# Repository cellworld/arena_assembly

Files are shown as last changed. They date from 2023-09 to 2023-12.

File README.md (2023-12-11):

# Cellworld Arena Assembly
<!-- ![Alt Text](https://github.com/cellworld/arena_assembly/blob/main/Images/cellworld_components-01.png) -->
<p align="center">
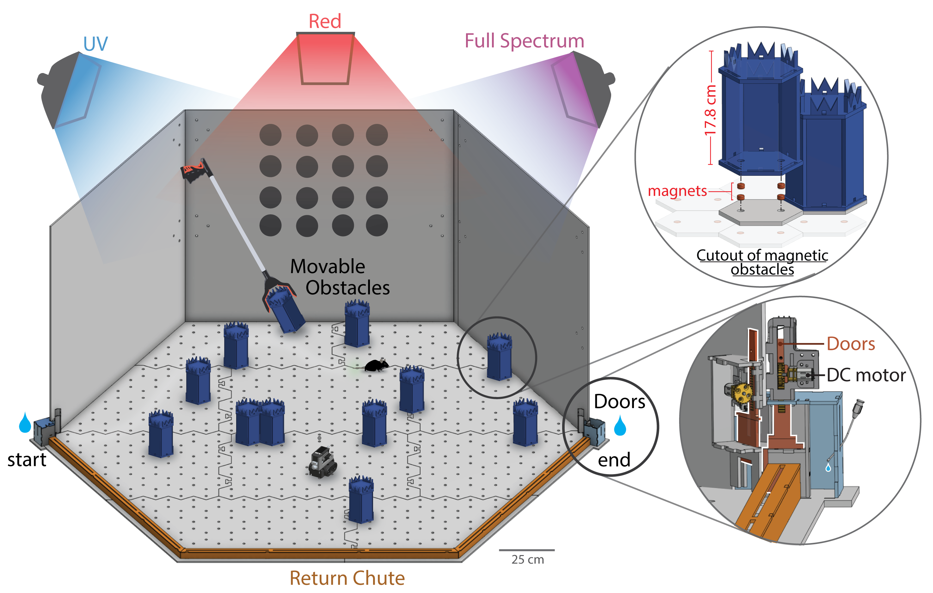
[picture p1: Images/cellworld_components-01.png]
arena_overview
  
</p>

All parts of the arena can be found in the STEP files of this github repository. <b>However, to see how the parts assemble on 
a web browser, you can use this [Onshape link](https://cad.onshape.com/documents/c8897f9f1e8291dd2da7ef89/w/1c35d23167742132946594eb/e/1fb43747d3ac53d540c92c7f?renderMode=0&uiState=64f8d54faca3cb0d59202402z)</b>.

Files in this repository are based on the Onshape CAD file system where we designed components in part studios and then imported them into assemblies 
to determine their interaction with other parts. Assemblies are good for visualizing how components are placed together for construction. 
When using the Onshape link, the assemblies will be the first files you will see, and
you can both manipulate objects within the assemblies and export them (as well are parts from the part studios) to whatever file format you need. 
For creating drawings for laser cutting or STL files for 3D printing however, we recommend using our part studios files.

Components of the arena can be devised into four components: the arena itself, the automated door system, the obstacles, and the water feeder system. 
Construction within each of these categories will be described below, but all parts are derived from either laser-cut acrylic or 3D printing.
Parts that need to be 3D printed will have the string "3D_PRINT" inserted at the beginning of the part's name.
Step files will have multiple parts included in them.

## The Arena
The arena consists of the arena floor, arena walls, general chamber structures, and the return chute. 
Please use the *Final Arena.step*  to grab all the parts. The one arena wall
opposite of the return chute center is replaced by the *Human Door.step* to allow for easy entry of the researcher. 

With exception to the wall binders (which are 3D printed), all parts are cut from white acrylic. All chamber and return chute components (the walls and ceilings) 
use 3.175 mm thick white acrylic, but all other parts use 6.35 mm thick white acrylic.

Please refer to the *Cellworld Arena.step* file in the *Assemblies* directory to see how all parts should fit.

Specialized Parts:
* 11.11 mm diameter neodymium magnets (D74-N52, K&J Magnetics, Pipersville, PA, USA)
* Red light bulbs (LED Red light therapy bulb, Wolezek LED, China)
* Full spectrum growth lights (9-Watt LED Grow Light Bulb, General Electric, Boston, MA, USA)
* UV light bulbs (UV LED Black lights Bulb, SHGPODA, Shenzhen, Guangdong, China)
* White noise generator (LectroFan Classic, Campbell, CA, USA)

Construction:
1. Assemble floor panels together and insert magnets into floor slots with superglue.
2. Assemble *Human Door.step* using 80/20 25.4 mm aluminum as a frame. Hinges can be added to the aluminum frame for the door.
2. Slot walls and human door into the floor.
2. Attach 3D-printed wall binders using bolts to connect walls together.
3. Add layer of hand-cut clear vinyl (to the shape of the arena) over arena floor.
4. Seal connections between arena walls and 3.175 mm thick clear vinyl floor with silicone sealant.
5. Slot chamber walls and return chute walls into floor.
6. Seal connections between chamber/return chute walls and the floor with silicone sealant.
7. Attach chamber and return chute ceilings. For return chute ceilings we added sticky magnets to the outside of the
arena walls and to the return chute ceiling for easy attachment.
8. Bond introduction chamber walls (minus the "Introduction Sliding Wall") together with the introduction chamber floor using liquid solvent for acrylic bonding (#4 Acrlyic Adhesive, Weld-On, Compton, CA, USA).
9. Insert magnets using superglue into "Introduction Chamber Wall" and the "Introduction Door Blocker".
10. Place light bulbs in the softbox and place in the arena.
11. Mount white noise generator near arena and above the arena walls.

## The Door System
This is the most complex component of the arena to assemble. Three main STEP files will be used to create the structure of the doors:
*END Door Housing.step*, *START outer door support.step*, and *START inner door support.step*. 
To note, all these components are associated with either the START or END chamber (indicated by their name), 
however, all parts can work with both chambers as they are simply mirrored before construction. 
In many cases, this might mean simply flipping parts during assembly.

Files labeled as the "door support" are the components that hold the 
DC motors, limit switches, and silicone/laser cut doors, keeping them in place so that the gear on the motors precisely interacts with the rail inserted into the doors. 
There are two doors associated with each chamber: inner doors control movement between the arena and chamber while outer doors control movement between
the chambers and the return chute. The door supports are housed in one large "door housing" that prevents the mouse
from interacting with electronic components. 

All parts are either 3D-printed or laser-cut using 3.175 mm thick white acrylic. 
To see how everything is assembled, refer to  *Full Door Setup.step* in the *Assemblies* directory,
but note that this is showing the assembly for the END chamber (mirrored to the part studio files). 

Specialized Parts:
* DC motors (50:1 6V micro metal gearmotor, Pololu, Las Vegas, NV, USA)
* Plastic motor holders (Micro Metal Gearmotor Bracket Extended Pair, Pololu, Las Vegas, NV, USA)
* DC motor gear hubs (Universal Aluminum Mounting Hub for 3mm Shaft, M3 Holes, Pololu, Las Vegas, NV, USA)
* Motor driver (DRV8833 Dual Motor Driver Carrier, Pololu, Las Vegas, Nevada, USA, part no. 2130)
* Limit switches (Micro Limit Switch 3Pins, TIAIHUA, China)

Construction:
1. Mirror *END Door Housing.step* and cut parts.
2. Assemble mirrored *END Door Housing.step*.
   1. Bond together all parts except for the "roof" and "ArenaEnclosure" parts using liquid solvent for acrylic bonding (#4 Acrlyic Adhesive, Weld-On, Compton, CA, USA)
and superglue (for when parts need more support).
   2. Bond together all "ArenaEnclosure" parts.
   3. Slot in roof, but leave this unglued.
3. Assemble *START outer door support.step*.
   1. Bond together all acrylic parts of the outer door support. 
   2. Insert limit switches into "3D_PRINT Switch Holder" such that the button is facing towards open slot, securing with screws. 
   3. Bolt down limit switch holder to bonded door support structure.
   4. Attach the "3D_PRINT DC Motor Spacer" by slotting it into the door support. 
   5. Attach the Pololu DC motor gear hubs to the Pololu DC motors. 
   6. Screw down the *3D_PRINT DC_Gear.step* into the gear hubs and motor using M3 screws. 
   7. Place motor on top of the spacer/door support and add the Pololu plastic motor holders, bolting them with the provided Pololu nuts and bolts. 
   8. Superglue *3D_PRINT DC_Teeth.step* into open slot of "Outer Door Silicone Holder" in *Outer Door.step*. 
   9. Superglue 1.5875 mm thick white neoprene rubber cut to the size of the "Silicone Extension" in *Outer Door.step* to the "Outer Door Silicone Holder". 
   10. Slide the assembled *Outer Door.step* into the door support. 
   11. Insert bolt into *Outer Door.step* and secure with nut. Bolt should be able to press limit switches as the door goes up and down. 
4. Assemble *START inner door support.step*
   1. Bond together all acrylic parts of the outer door support except the "Inner Door Silicone Holder". 
   2. Insert limit switched into "3D_PRINT Switch Holder", securing with screws. 
   3. Bolt down limit switch holder to bonded door support structure. 
   4. Attach the "3D_PRINT DC Motor Spacer" in *START outer door support.step* by slotting it into the door support. 
   5. Attach the Pololu DC motor gear hubs to the Pololu DC motors. 
   6. Screw down the *3D_PRINT DC_Gear.step* into the gear hubs and motor using M3 screws. 
   7. Place motor on top of the spacer/door support and add the Pololu plastic motor holders, bolting them with the provided Pololu nuts and bolts. 
   8. Superglue *3D_PRINT DC_Teeth.step* into open slot of "Inner Door Silicone Holder". 
   9. Superglue 1.5875 mm thick white neoprene rubber to the "Inner Door Silicone Holder"
   10. Slide the assembled "Inner Door Silicone Holder" into the door support. 
   11. Insert bolt into the "Inner Door Silicone Holder" and secure with nut. Bolt should be able to press the limit switch when the door is moving down. 
5. Wire motors and limit switches based on *door_water_feeder_electronics.zip* in the *Electronics* directory, making sure that wires connecting limit switches and motors to the motor drivers
are detachable. 
6. Insert the assembled mirrored *END Door Housing.step* (from step 2i; without the "ArenaEnclosure" and roof) into the START chamber. 
7. Insert the assembled *START outer door support.step* and *START inner door support.step* into the Door Housing.
8. Add the "ArenaEnclosure" of the mirrored *END Door Housing.step* (from step 2ii) around *START inner door support.step* and attach roof. 
9. Connect the limit switches and motors to the motor drivers. 
10. Repeat steps 1-9 for the END chamber using mirrored START parts.

## The Obstacles
All obstacles are laser cut using 6.35 mm thick white acrylic. 
To see how everything is assembled, refer to  *Exploded Obstacle.step* in the *Assemblies* directory.

Specialized Parts:
* 11.11 mm diameter neodymium magnets (D74-N52, K&J Magnetics, Pipersville, PA, USA).

Construction:
* For each obstacle, laser cut 1 "Occlusion Base", 1 "Occlusion Top", and 6 "Occlusion Walls".
* Attach magnets into the "Occusion Base" using super glue
* Assemble and bond all parts together using liquid solvent for acrylic bonding (#4 Acrlyic Adhesive, Weld-On, Compton, CA, USA).

## The Water Feeders
All water feeder parts listed in this repository are 3D-printed. 

Specialized Parts:
* Solenoids 
  * We use this solenoid: 2-way Normally Closed Isolation Valve, part number 161T012, NResearch, West Caldwell, NJ, USA
  * However, we recommend using these (this may require changes to the solenoid holder part): 
  Miniature Solenoid Valves Normally Closed 24V, part number 5001T36, McMaster-Carr, Elmhurst, IL, USA
* Capacitive Sensor (AT42QT1011, SparkFun, Boulder, CO, USA)
* Water Spout (Curved Feeding Needles 18 Gauge, part number FNC-18-2-2, Kent Scientific, Torrington, CT, USA)
* Tubing (Tygon S3 E-3603, 1/16 in Inside Dia. 1/8 in Outside Dia., Saint-Gobain, Courbevoie, France)
* Mosfet (RFP30N06LE 30A 60V N-Channel Power Mosfet, WeiMeet, China)

Construction:
1. Place a 60mL syringe, into the *3D_PRINT Water Reservoir Holder.step*
2. Secure the water reservoir 1m above the ground.
3. Place solenoid inside *3D_PRINT Solenoid Holder.step*
4. Secure the solenoid ~30cm above the ground between water reservoir and chamber 
5. Attach wire to water spout using heat shrink wrap. 
6. Secure *3D_PRINT Feeder Holder.step* to chamber walls and insert water spout. 
7. Attach tubing between water spout, solenoid, and water reservoir. 
8. Connect electronics based on *door_water_feeder_electronics.zip* in the *Electronics* directory.
9. Repeat steps 1-8 for other chamber.

## Electronics
<!-- ![Alt Text](https://github.com/cellworld/arena_assembly/blob/main/Images/maze1_circuit_diagram.png) -->
<p align="center">
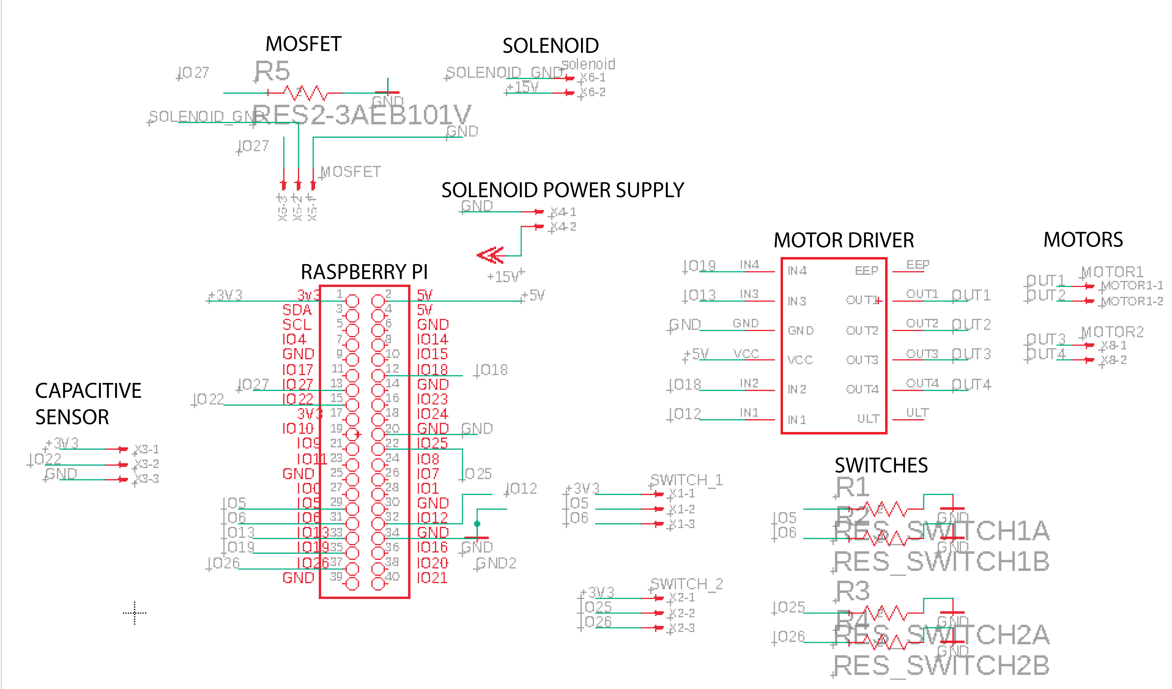
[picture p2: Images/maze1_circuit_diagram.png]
circuit_diagram
  
</p>

For connecting all systems together, please follow the EAGLE circuit diagram shown in *door_water_feeder_electronics.zip*.

Specialized Parts:
* Raspberry Pis (3B+, Raspberry Pi, Cambridge, England, UK)

## Code
Relevant code for the arena doors and water feeders resides in separate repositories:

* Code installed on Raspberry Pis (creates services for doors and the water feeder):
[https://github.com/cellworld/cellworld_habitat_pi](https://github.com/cellworld/cellworld_habitat_pi)
* Terminal to control and connect to doors and water feeder:
[https://github.com/cellworld/cellworld_habitat_controller](https://github.com/cellworld/cellworld_habitat_controller)

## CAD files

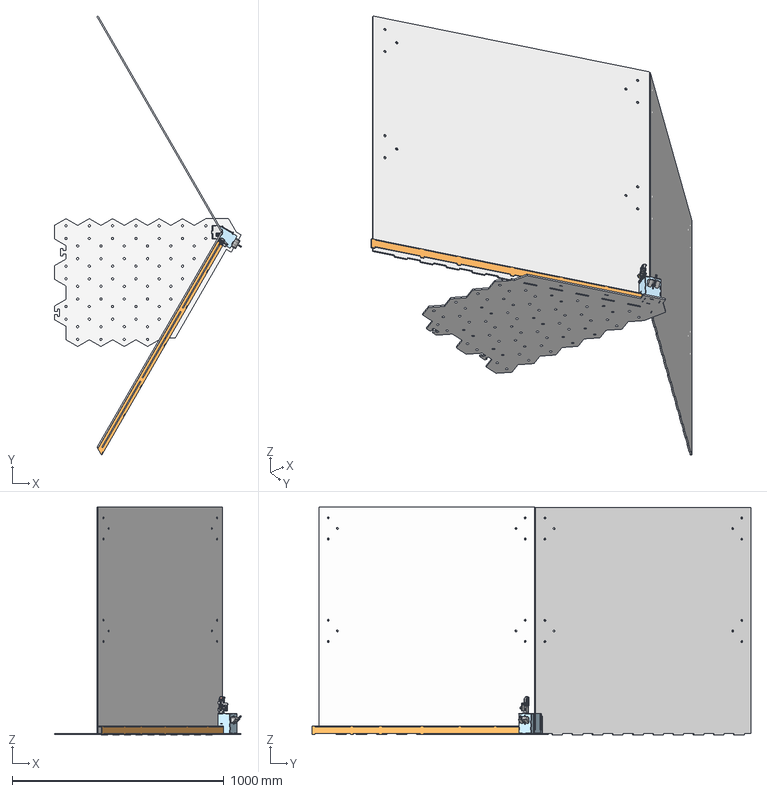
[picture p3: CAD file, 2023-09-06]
Assemblies/Full Door Setup.step
884.0 x 2071.9 x 1074.0 mm
arch1
Top Wall Extension 4
Frontwall
Top Wall Extension 2
Limit Switch - Micro Switch x 4
Micro Metal Gear Motor x 22
3D_PRINT DC motor Spacer
ChamberTopWall
3D PRINT gear x 2
3D_PRINT Door0 Key
Outer Door Silicone Holder
Return Floor Plug
ChamberBottomWall x 3
archside
Chamber Top Wall 2
Sliding Top Wall
ChamberCeiling
Top Wall Extension 1
enclosure2
Wall1
3D_PRINT Feeder Holder
enclosure
3D_PRINT rail x 2
ChamberRightWall
Sidewall2
Top Wall Extension 3
Water Spout
floor
enclosure1
arch2
ReturnChuteSeiling1
Third
Wall6
First
Riel2
roof
Silicone Extension
P7
Riel1
ReturnChute1
Sidewall1

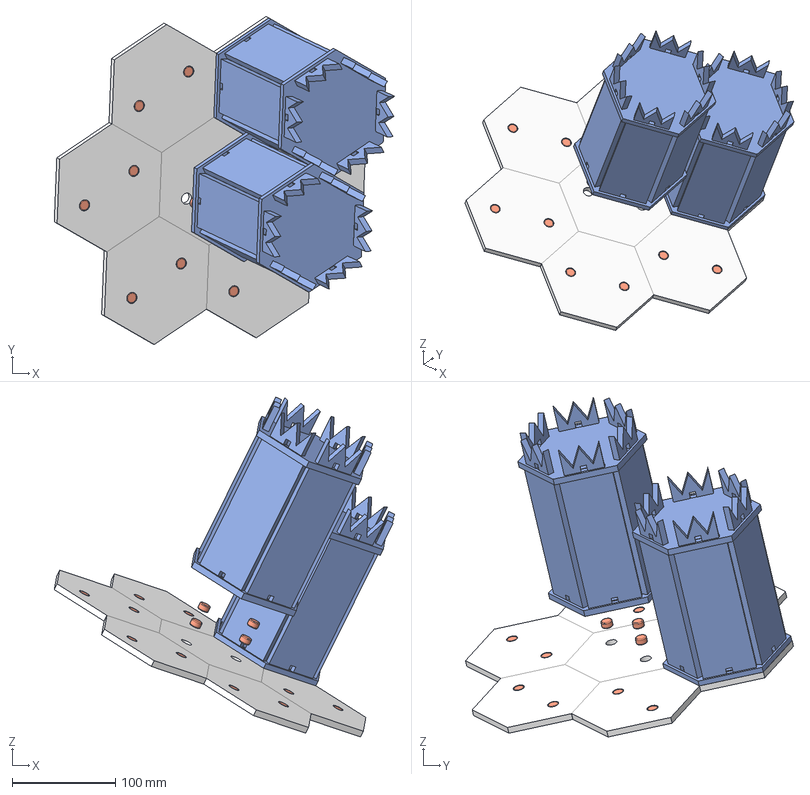
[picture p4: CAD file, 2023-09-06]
Assemblies/Exploded Obstacle.step
330.0 x 317.9 x 329.5 mm

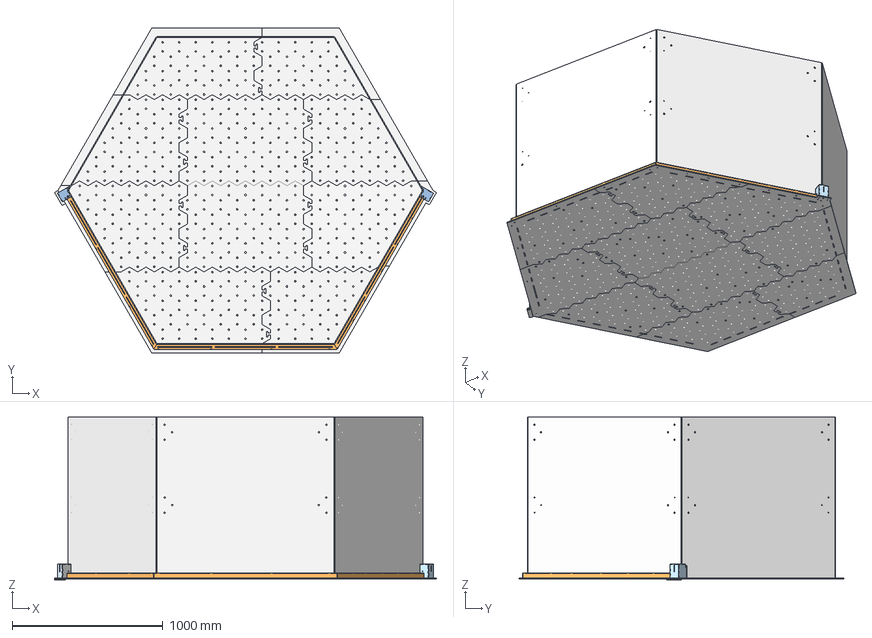
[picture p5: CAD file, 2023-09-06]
Part Studios/Arena/Arena For Figures.step
2533.5 x 2154.7 x 1079.5 mm

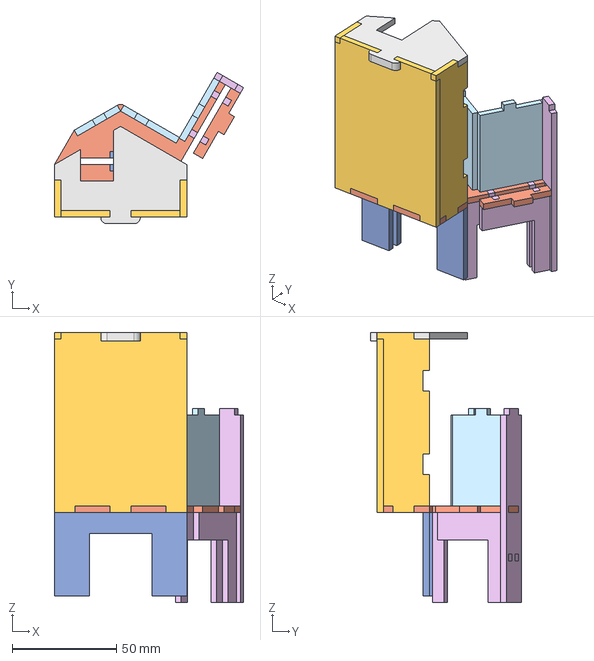
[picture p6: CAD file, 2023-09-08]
Part Studios/Door System/END Door Housing.step
90.8 x 72.6 x 129.5 mm

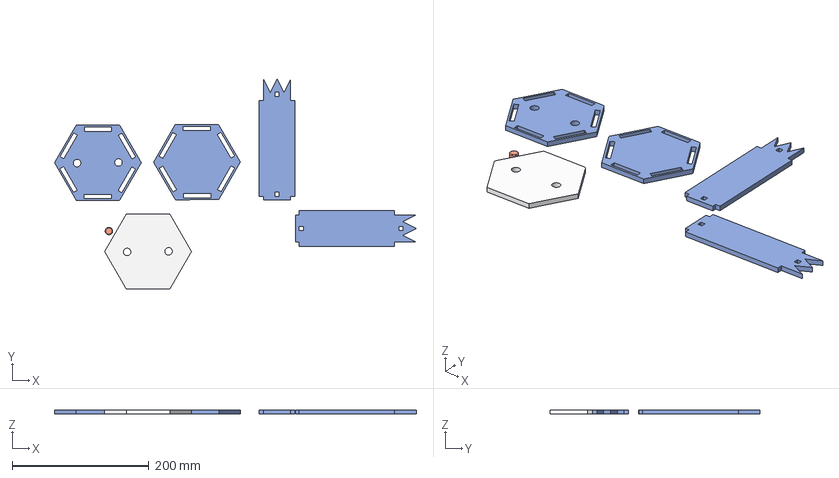
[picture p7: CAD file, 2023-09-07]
Part Studios/Obstacles/Occlusion Parts.step
529.3 x 307.5 x 6.35 mm

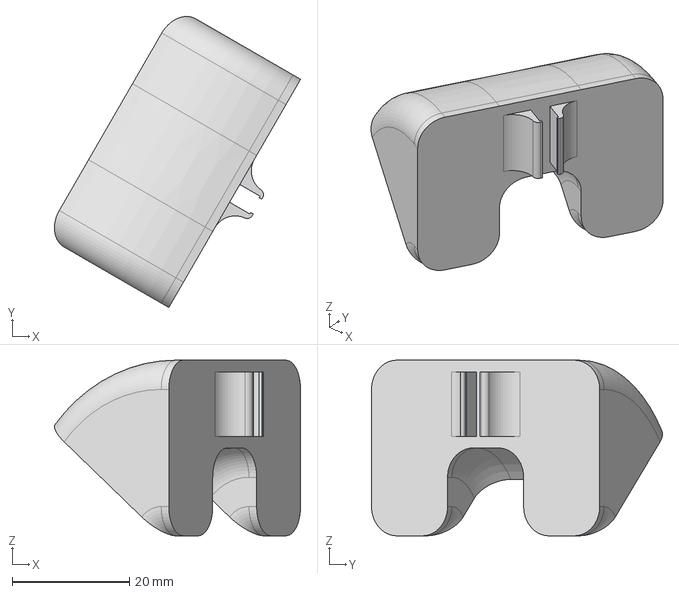
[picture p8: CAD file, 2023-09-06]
Part Studios/Water Feeder/3D_PRINT Feeder Holder.step
42.0 x 49.7 x 30.0 mm

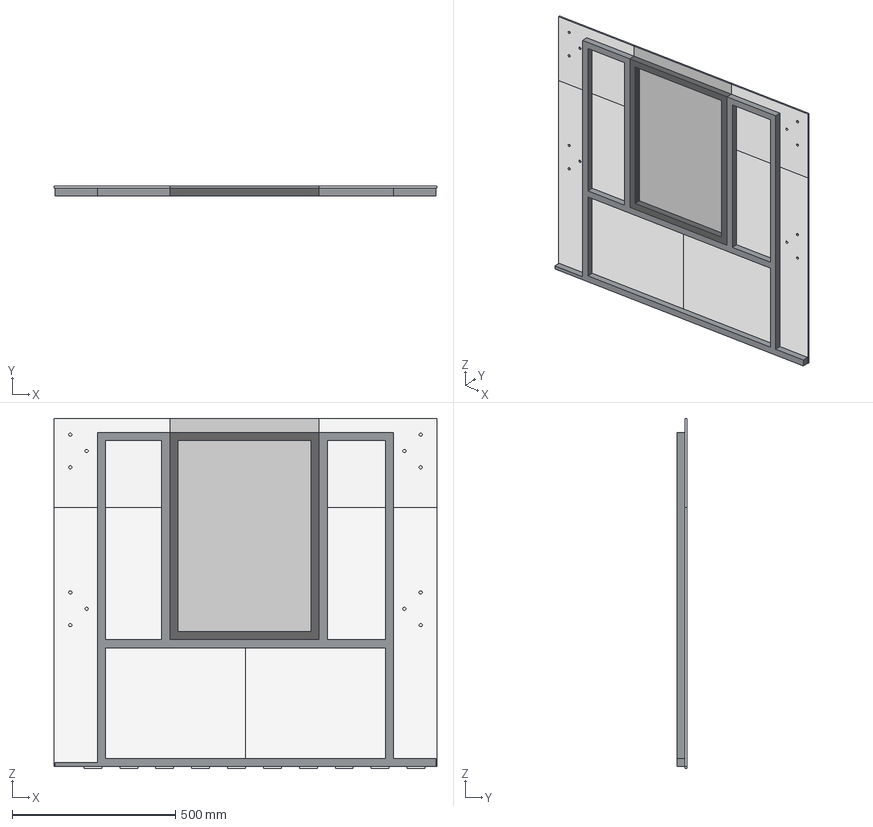
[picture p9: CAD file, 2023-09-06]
Part Studios/Arena/Human Door.step
1173.2 x 31.8 x 1073.1 mm

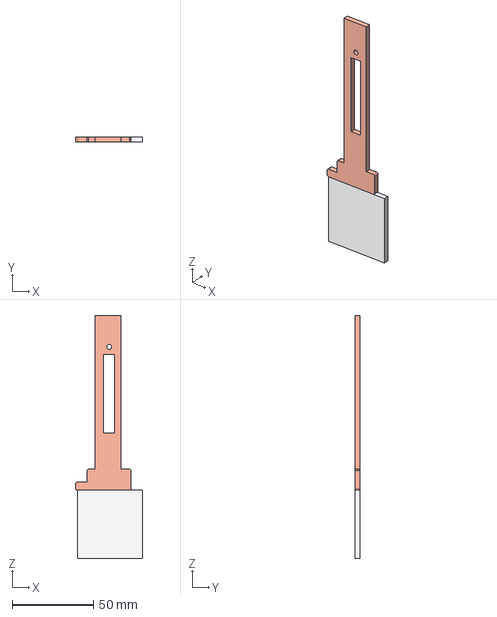
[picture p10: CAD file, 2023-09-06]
Part Studios/Door System/Outer Door.step
41.0 x 3.18 x 149.4 mm

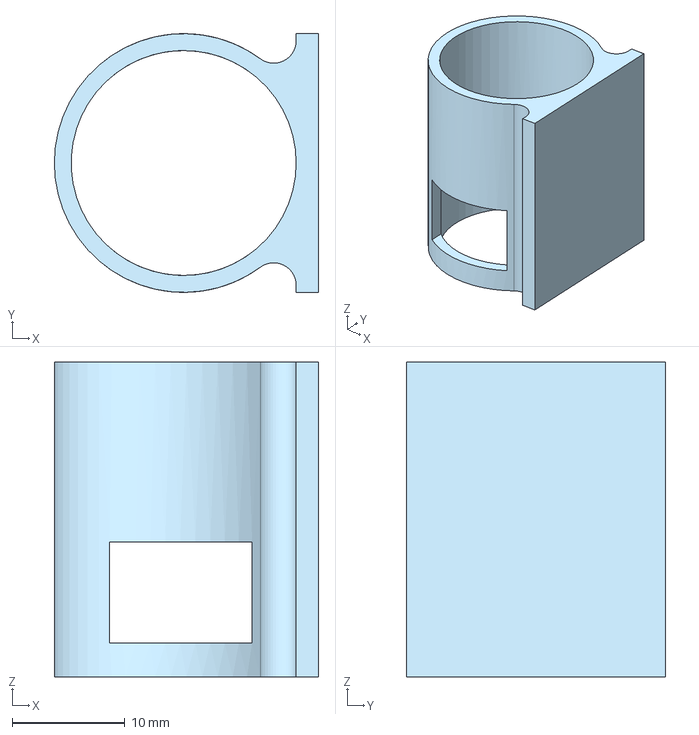
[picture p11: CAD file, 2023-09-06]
Part Studios/Water Feeder/3D_PRINT Solenoid Holder.step
23.5 x 23.0 x 28.0 mm

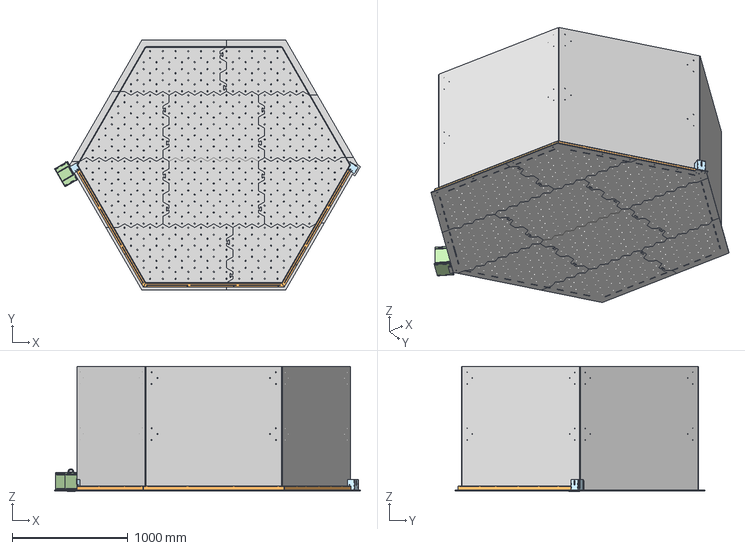
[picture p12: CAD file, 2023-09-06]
Part Studios/Arena/Final Arena.step
2641.7 x 2154.7 x 1079.5 mm

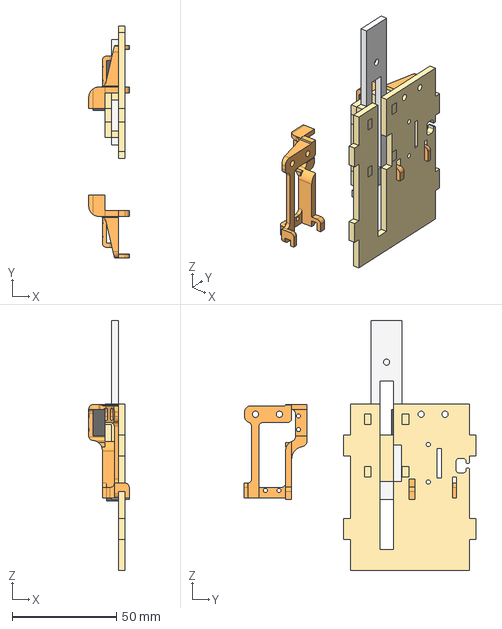
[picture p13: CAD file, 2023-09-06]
Part Studios/Door System/START inner door support.step
19.5 x 111.3 x 120.0 mm

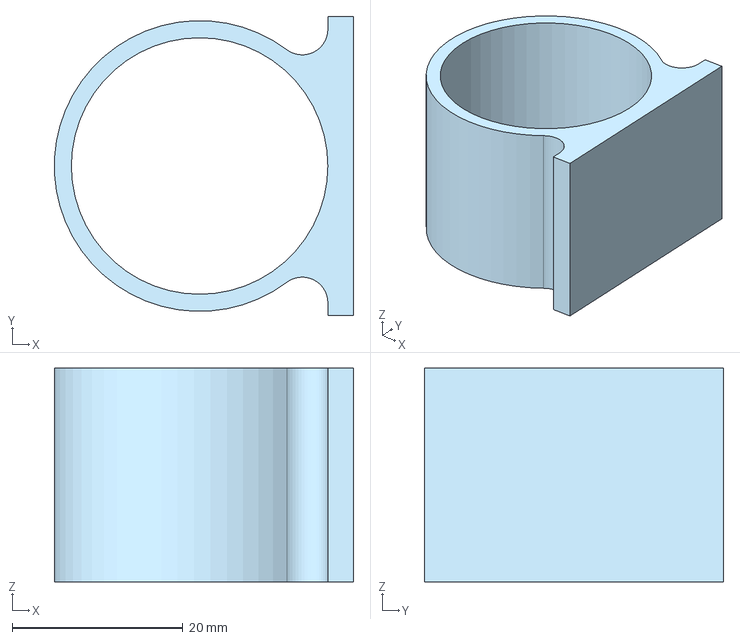
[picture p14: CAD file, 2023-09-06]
Part Studios/Water Feeder/3D_PRINT Water Reservoir Holder.step
35.0 x 35.0 x 25.0 mm

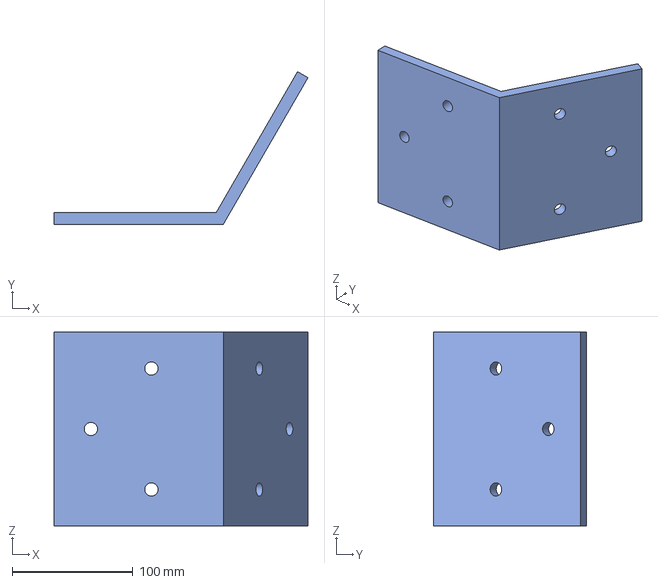
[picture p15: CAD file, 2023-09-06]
Part Studios/Arena/3D_PRINT WallBrackets.step
210.0 x 126.2 x 160.0 mm

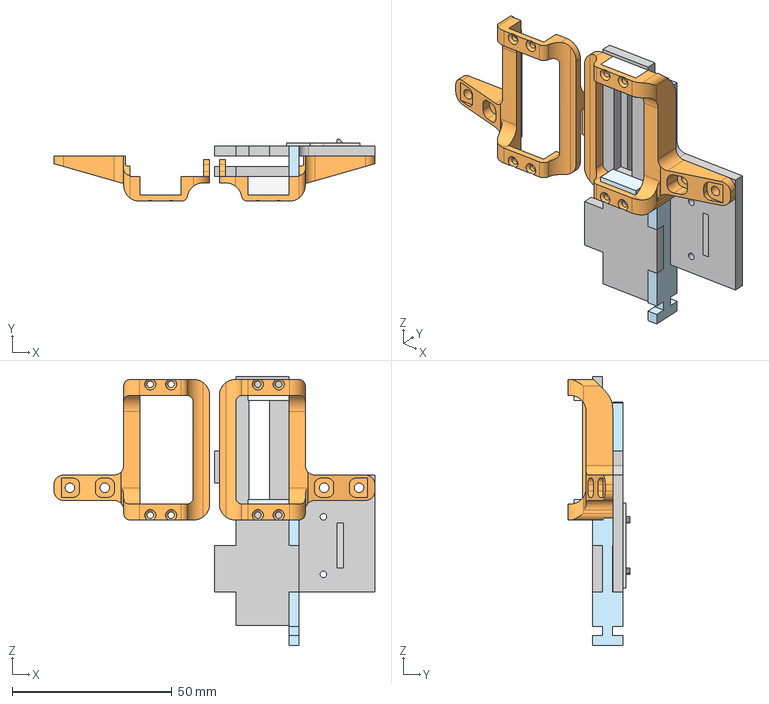
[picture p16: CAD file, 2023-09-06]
Part Studios/Door System/START outer door support.step
100.5 x 19.6 x 84.4 mm

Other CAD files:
Part Studios/Door System/3D_PRINT DC_Teeth.step
Part Studios/Door System/3D_PRINT DC_Gear.step
Part Studios/Door System/3D_PRINT Flag Motor Lock.step

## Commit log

2023-09-06 Adding CAD files
    [3D_PRINT DC_Gear.step, 3D_PRINT DC_Teeth.step, 3D_PRINT Feeder Holder.step, 3D_PRINT Flag Motor Lock.step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]
2023-09-06 Altered CAD files and added more text
    [3D_PRINT DC_Gear.step, 3D_PRINT DC_Teeth.step, 3D_PRINT Feeder Holder.step, 3D_PRINT Flag Motor Lock.step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]
2023-09-07 Added electronics folder, changed to occlusions parts, and text
    [Occlusion Parts.step]
2023-09-07 Moved raspberry pis to electronics
2023-09-08 Fixed some typos
    [END Door Housing.step, START Door Frame.step]
